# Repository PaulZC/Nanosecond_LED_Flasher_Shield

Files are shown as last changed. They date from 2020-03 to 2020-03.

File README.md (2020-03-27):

# Nanosecond LED Flasher Shield
 
A nanosecond LED flasher which provides digital control of both pulse width and LED current. Designed to aid
photomultiplier detector characterisation.
 
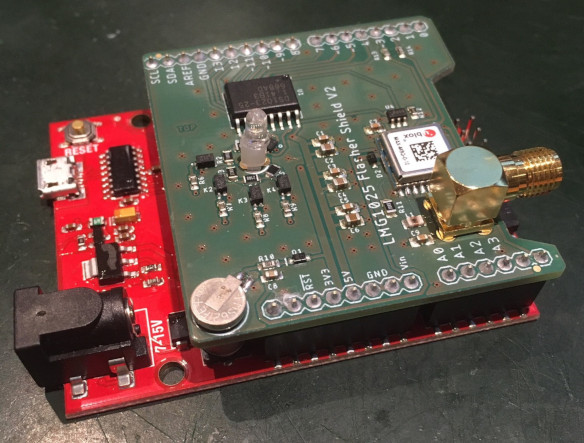
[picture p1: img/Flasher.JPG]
Flasher


The LED is driven by the new [LMG1025 from Texas Instruments](http://www.ti.com/product/LMG1025-Q1).
Designed for automotive LIDAR applications, this gate driver has typical rise and fall times of 650ps
and 850ps and can produce 5V pulse widths as short as 1.25ns.

The pulse width is controlled by a [Maxim Integrated DS1023S-25+](https://www.maximintegrated.com/en/products/analog/clock-generation-distribution/DS1023.html)
programmable timing element which can produce digitally-adjustable pulse widths of 0 to ~64ns in 0.25ns increments.

The LED current is set by five surface mount resistors connected in series, four of which can be shorted
out by [Toshiba TLP3475 photorelays](https://toshiba.semicon-storage.com/ap-en/semiconductor/product/optoelectronics/photorelay-mosfet-output/detail.TLP3475.html)
allowing the LED current to be adjusted digitally in 16 increments.

The shield also uses a [u-blox MAX-M8Q GNSS module](https://www.u-blox.com/en/product/max-m8-series) as a
signal generator to dictate the flash rate. The flash rate can be set to any frequency between 0.25Hz
and 10MHz.

The shield is designed to be mounted on a [5V ATmega328 Arduino Uno or similar](https://www.sparkfun.com/products/13975).
(Please note that the shield requires 5V I/O signals for correct operation and will not work if mounted
on a 3.3V Arduino Zero or similar.)

## Example Performance

In the image below:
- the yellow trace shows the anode voltage of a Bivar UV3TZ-400-15 UV LED being driven by the shield at maximum brightness (equivalent series resistance approx. 14 ohms) (1V per division)
- the green trace shows the corresponding fast output of a SensL J-series silicon photomultiplier (50mV per division)
- the timebase is 2 nsec per division

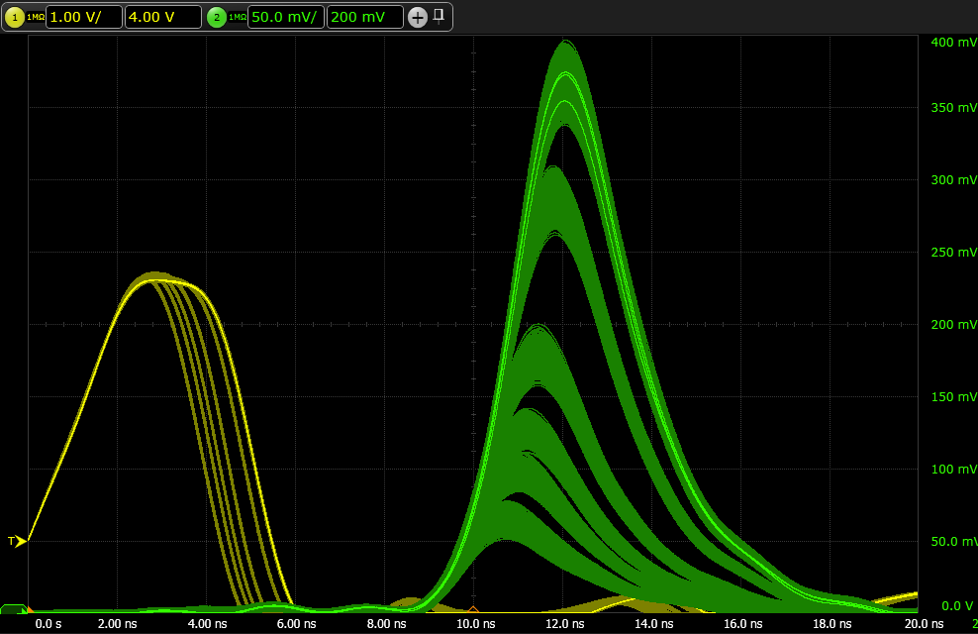
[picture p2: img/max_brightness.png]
max_brightness


The overlapping yellow traces show the LED pulse width being increased in 0.25 nsec increments. The corresponding green traces show how the peak output of
the SiPM increases in line with the LED pulse width and the number of photons emitted during each pulse.

## Repository Contents

- **/Documentation** - Documentation for the hardware and software
- **/Hardware** - BOM, schematic and Eagle PCB design files
- **/Software** - Arduino code
- **LICENSE.md** contains the licence information

## Documentation

- [Hardware overview](https://github.com/PaulZC/Nanosecond_LED_Flasher_Shield/blob/master/Documentation/Hardware/README.md): an overview of the hardware
- [Software user guide](https://github.com/PaulZC/Nanosecond_LED_Flasher_Shield/blob/master/Documentation/Software/README.md): a user guide for the Arduino code

Enjoy!

**_Paul_**

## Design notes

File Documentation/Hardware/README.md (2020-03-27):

# Nanosecond LED Flasher Shield: Hardware Overview
 
A nanosecond LED flasher which provides digital control of both pulse width and LED current. Designed to aid
photomultiplier detector characterisation.

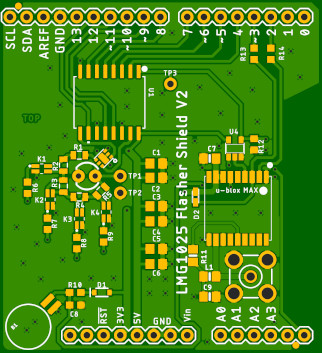
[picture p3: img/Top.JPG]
Top


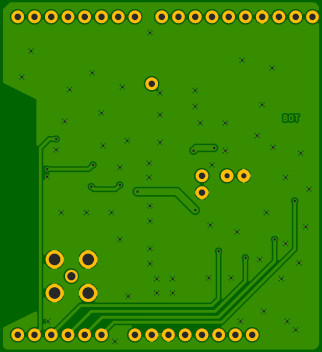
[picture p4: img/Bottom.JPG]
Bottom


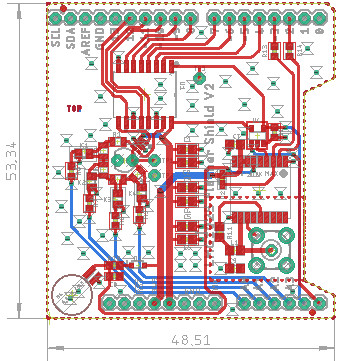
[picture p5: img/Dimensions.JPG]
Dimensions


The full schematic is available [here](https://github.com/PaulZC/Nanosecond_LED_Flasher_Shield/blob/master/Hardware/Schematic.pdf).

The BOM is available in [PDF format](https://github.com/PaulZC/Nanosecond_LED_Flasher_Shield/blob/master/Hardware/BOM.pdf)
and [ODS format](https://github.com/PaulZC/Nanosecond_LED_Flasher_Shield/blob/master/Hardware/BOM.ods).

The LED is driven by the new [LMG1025 from Texas Instruments](http://www.ti.com/product/LMG1025-Q1).
Designed for automotive LIDAR applications, this gate driver has typical rise and fall times of 650ps
and 850ps and can produce 5V pulse widths as short as 1.25ns.

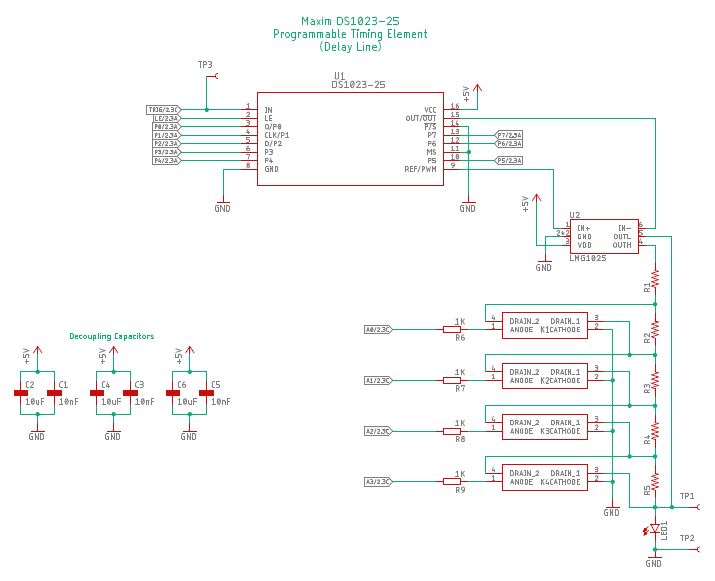
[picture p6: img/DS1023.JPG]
DS1023


The functional block diagram for the LMG1025 is:

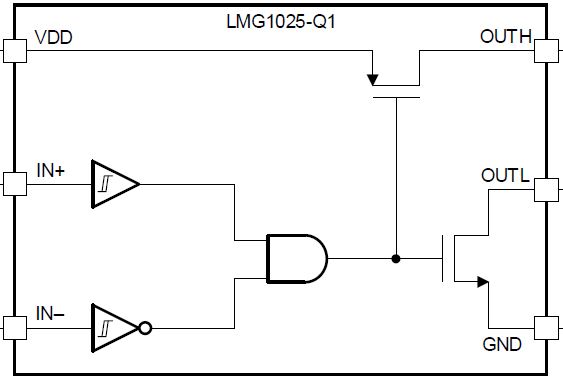
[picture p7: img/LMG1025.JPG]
LMG1025


The LMG1025 is designed to drive a GaN FET to switch a LIDAR source, but with pull-up and pull-down
current limits of 7A and 5A it can of course drive a standard or high-brightness LED directly.

The truth table for the LMG1025 is:

Truth Table

It is important to note that OUTH is pulled up to 5V only when IN+ is high and IN- is low. In each of the other
three possible states, OUTL is pulled low. We can take advantage of this by connecting OUTH to the current-limiting
resistor and OUTL directly to the LED anode. This allows the LED to be turned off very quickly.

The Maxim Integrated DS1023S-25+ is a programmable timing element with two outputs: OUT and REF. The delay between IN and
OUT is digitally-programmable from 0ns to ~64ns in 256 0.25ns increments. There is also an additional inherrent "step zero"
delay between IN and OUT caused by the propagation delay through the chip. The REF output is delayed by a small fixed delay
of approximately 1.5ns plus the same "step zero" delay. By driving the LMG1025 IN+ and IN- from REF and OUT respectively,
the LED pulse can be adjusted from essentially zero pulse width (+/-0.125ns) to a maximum of 62.5ns (64ns - 1.5ns).
The LED turns on when REF goes high, and off again when OUT goes high.

Five resistors, connected in series, are connected between the LMG1025 OUTH pin and the LED anode. By shorting out four
of these resistors in 16 permutations, the LED current can be adjusted between minimum and maximum values dictated by
the selection of resistor values. The resistors are shorted out by TLP3475 photorelays which provide fast response times
and an on-resistance of approximately 1ohm.

For example: with resistances of 10, 18, 22, 27 and 33 ohms, with the 10 ohm resistor always in circuit, it is possible to achieve
an even spread of resistance values from 13.8 ohms to 110 ohms.

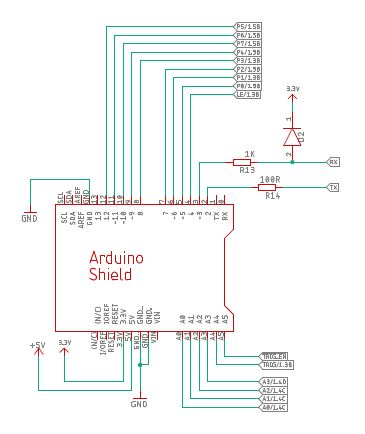
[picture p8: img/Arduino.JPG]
Arduino


The ATmega328 Arduino: controls the LED pulse width, by setting the eight parallel lines which set the DS1023 delay;
the pulse brightness, by selecting which of the four photorelays are enabled; and the pulse frequency, by setting the
frequency of the MAX-M8Q GNSS module TIMEPULSE pin. Pulse frequencies of 0.25Hz to 10MHz are possible.

The Arduino pin allocation is:
- D0: reserved for Serial Rx
- D1: reserved for Serial Tx
- D2: software serial Rx - receives GNSS data from the MAX-M8Q
- D3: software serial Tx - transmits configuration messages to the MAX-M8Q
- D4: DS1023 Latch Enable
- D5: DS1023 delay bit 0
- D6: DS1023 delay bit 1
- D7: DS1023 delay bit 2
- D8: DS1023 delay bit 3
- D9: DS1023 delay bit 4
- D10: DS1023 delay bit 7
- D11: DS1023 delay bit 6
- D12: DS1023 delay bit 5
- D13: reserved for LED_BUILTIN (but can also be used to indicate the reception of the GNSS time pulses)
- A0/D14: the photorelay for R2
- A1/D15: the photorelay for R3
- A2/D16: the photorelay for R4
- A3/D17: the photorelay for R5
- A4/D18: the MAX-M8Q time pulse (to allow the LED current to be changed between LED pulses)
- A5/D19: enables / disables LED pulses via the 74HCT1G125 buffer

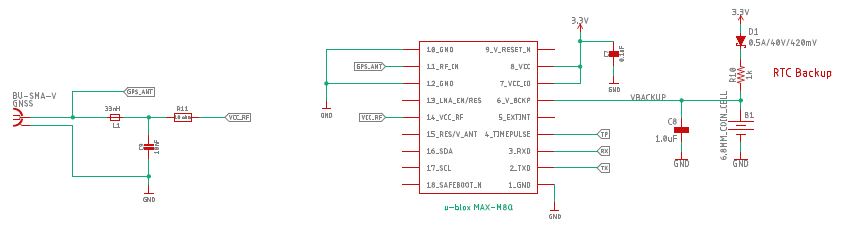
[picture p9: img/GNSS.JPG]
GNSS


The time pulse signal produced by the MAX-M8Q GNSS receiver is used to trigger the DS1023. The frequency of the time pulse
signal can be defined by the Arduino code via software serial (D2 and D3). The LED flashes on the rising edge of the time pulse.
The time pulse signal is connected to the Arduino pin A4/D18 so that the LED current can be adjusted between pulses on the
falling edge of the signal. It is possible to change the current for adjacent LED pulses from one of the sixteen permutations
to any other. The Arduino code can produce repetitive pulse patterns using any of the sixteen states.

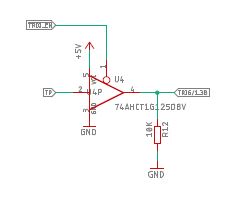
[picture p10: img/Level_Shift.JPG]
Level_Shift


The MAX-M8Q is a 3.3V device. A 74HCT1G125 buffer is used to convert the 3.3V time pulses to 5V for the DS1023. The enable pin
of the buffer is connected to Arduino pin A5/D19 such that pulses can be skipped or disabled as required.

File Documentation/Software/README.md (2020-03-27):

# Nanosecond LED Flasher Shield: Software Overview
 
The Arduino code for the nanosecond flasher is available [here](https://github.com/PaulZC/Nanosecond_LED_Flasher_Shield/tree/master/Software/LMG1025_Flasher).

Please ensure you select _Arduino Uno_ as the Board.

The code has been deliberately kept very simple. It begins by setting the MAX-M8Q time pulse pin to the desired frequency.
You will find definitions in the code for frequencies of 60Hz, 500Hz, 1kHz, 10kHz, 100kHz and 1MHz.

Also defined in the code are sequences of LED pulse brightnesses (currents) that can be used if desired. By default,
the brightness sequence is disabled. You can enable one by uncommenting _#define useSequence_ plus one of the
definitions for _sequence_.

The LED pulse width and current can be configured by sending a serial string to the Arduino, via the Serial Monitor.
The Serial baud rate should be set to 9600. Set the line ending to LF. The serial data format is:
- ASCII <                : 3C Hex
- Pulse Delay P7 (MSB)   : ASCII 0 or 1 (30 or 31 Hex)
- Pulse Delay P6         : ASCII 0 or 1 (30 or 31 Hex)
- Pulse Delay P5         : ASCII 0 or 1 (30 or 31 Hex)
- Pulse Delay P4         : ASCII 0 or 1 (30 or 31 Hex)
- Pulse Delay P3         : ASCII 0 or 1 (30 or 31 Hex)
- Pulse Delay P2         : ASCII 0 or 1 (30 or 31 Hex)
- Pulse Delay P1         : ASCII 0 or 1 (30 or 31 Hex)
- Pulse Delay P0 (LSB)   : ASCII 0 or 1 (30 or 31 Hex)
- LED R5                 : ASCII 0 or 1 (30 or 31 Hex) (0 = R is in circuit; 1 = R is shorted) (R5 is >> R2)
- LED R4                 : ASCII 0 or 1 (30 or 31 Hex) (0 = R is in circuit; 1 = R is shorted)
- LED R3                 : ASCII 0 or 1 (30 or 31 Hex) (0 = R is in circuit; 1 = R is shorted)
- LED R2                 : ASCII 0 or 1 (30 or 31 Hex) (0 = R is in circuit; 1 = R is shorted) (R2 is << R5)
- ASCII >                : 3E Hex
- LF                     : 0A Hex

e.g.:  <000100001111>\n will produce ~2.5ns pulses ((16 x 0.25ns) - 1.5ns) of maximum brightness (all four photorelays are on)

A shorter message can be sent if you only want to change the pulse width:
- ASCII <                : 3C Hex
- Pulse Delay P7 (MSB)   : ASCII 0 or 1 (30 or 31 Hex)
- Pulse Delay P6         : ASCII 0 or 1 (30 or 31 Hex)
- Pulse Delay P5         : ASCII 0 or 1 (30 or 31 Hex)
- Pulse Delay P4         : ASCII 0 or 1 (30 or 31 Hex)
- Pulse Delay P3         : ASCII 0 or 1 (30 or 31 Hex)
- Pulse Delay P2         : ASCII 0 or 1 (30 or 31 Hex)
- Pulse Delay P1         : ASCII 0 or 1 (30 or 31 Hex)
- Pulse Delay P0 (LSB)   : ASCII 0 or 1 (30 or 31 Hex)
- ASCII >                : 3E Hex
- LF                     : 0A Hex

e.g.:  <001000001111>\n will produce ~6.5ns pulses ((32 x 0.25ns) - 1.5ns)

The code will: parse the incoming serial data, check the format is valid, set the DS1023 pulse width,
and the state of the four photorelays.

The rise time of the LED forward voltage will depend on the resistance value. More resistance equals
slower rise times as well as lower current (and lower peak forward voltage too). The actual pulse width,
in terms of how long the LED is actually emitting photons for, is equal to the amount of time the forward voltage
exceeds approximately 3.1V (for the Bivar UV3TZ-400-15 400nm InGaN/Sapphire UV LED).

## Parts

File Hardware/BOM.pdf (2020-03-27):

LMG1025_Flasher_Shield

Page 1

Name X | Y | Angle Package | Value | Comments
FD1 | 2.29 52.45 | 0 FIDUCIAL
FD2 | 44.45 | 1.02 | 0 FIDUCIAL
B1 | 7.25 | 7.25 | 45 | MS621FE-FL11E | 1614634 | Rechargeable 3V 6.8mm Coin Cell Seiko MS621FE-FL11E
C1 | 23.24 28.58 | 0 0805 | 10nF | 2496939 | SMD Capacitor 10nF 50V 0805 +/-10% X7R
C2 | 23.24 26.42 | 0 0805 | 10uF | 1759421 | SMD Capacitor 10uF 10V 0805 +80% -20% Y5V
C3 | 23.24 | 22.1 | 0 0805 | 10nF | 2496939 | SMD Capacitor 10nF 50V 0805 +/-10% X7R
C4 | 23.24 19.81 | 0 0805 | 10uF | 1759421 | SMD Capacitor 10uF 10V 0805 +80% -20% Y5V
C5 | 23.24 15.62 | 0 0805 | 10nF | 2496939 | SMD Capacitor 10nF 50V 0805 +/-10% X7R
C6 | 23.24 13.34 | 0 0805 | 10uF | 1759421 | SMD Capacitor 10uF 10V 0805 +80% -20% Y5V
C7 | 31.37 29.34 | 180 0805 | 0.1uF | 2496944 | SMD Capacitor 100nF 50V 0805 +/-10% X7R
C8 | 10.92 | 7.11 | 0 0603 | 1.0uF | 1327684 | SMD Capacitor 1uF 10V 0603 +/-10% X5R
C9 | 31.37 | 8.38 | 0 0805 | 10nF | 2496939 | SMD Capacitor 10nF 50V 0805 +/-10% X7R
D1 | 14.99 | 9.02 | 0 SOD-323 | PMEG4005EJ | 1757776 | Schottky Rectifier 40V 500mA Nexperia PMEG4005EJ
D2 | 29.21 | 23.5 | 270 SOD-323 | PMEG4005EJ | 1757776 | Schottky Rectifier 40V 500mA Nexperia PMEG4005EJ
K1 | 5.84 27.79 | 270 | TLP3475 | Toshiba TLP3475 Photorelay (not TLP3475R) Mouser: 757-TLP3475TPF
K2 | 7.13 23.11 | 0 | TLP3475 | Toshiba TLP3475 Photorelay (not TLP3475R) Mouser: 757-TLP3475TPF
K3 | 11.58 20.19 | 0 | TLP3475 | Toshiba TLP3475 Photorelay (not TLP3475R) Mouser: 757-TLP3475TPF
K4 | 15.64 21.21 | 0 | TLP3475 | Toshiba TLP3475 Photorelay (not TLP3475R) Mouser: 757-TLP3475TPF
L1 | 31.37 11.43 | 0 0805 | 0805HT-33NTGLB | 2286465 | Surface Mount High Frequency Inductor; 0805; 33 nH; 600 mA
R1 | 11.56 29.85 | 0 0805 | Select on test: suggested value 10R
R2 | 9.14 28.32 | 90 0805 | Select on test: suggested value 18R
R3 | 9.14 25.15 | 90 0805 | Select on test: suggested value 22R
R4 | 11.56 | 23.5 | 180 0805 | | | Select on test: suggested value 27R
R5 | 14.86 24.38 | 225 0805 | Select on test: suggested value 33R
R6 | 3.68 24.89 | 270 0603 | 1K | 2447272 | SMD Chip Resistor; Thick Film; 1k; 75V; 0603; 100mW
R7 | 6.73 19.43 | 270 0603 | 1K | 2447272 | SMD Chip Resistor; Thick Film; 1k; 75V; 0603; 100mW
R8 | 11.18 16.51 | 270 0603 | 1K | 2447272 | SMD Chip Resistor; Thick Film; 1k; 75V; 0603; 100mW
R9 | 15.24 17.53 | 270 0603 | 1K | 2447272 | SMD Chip Resistor; Thick Film; 1k; 75V; 0603; 100mW
R10 | 10.92 | 9.02 | 0 0603 | 1k | 2447272 | SMD Chip Resistor; Thick Film; 1k; 75V; 0603; 100mW
R11 | 28.83 14.61 | 90 0805 | 10R | 1469859 | SMD Chip Resistor; Thick Film; 10 ohm; 150V; 0805; 100mW
R12 | 38.1 | 31.5 | 270 0603 | 10K | 2447230 | SMD Chip Resistor; Thick Film; 10K; 75V; 0603; 100mW
R13 | 38.1 45.21 | 90 0603 | 1K | 2447272 | SMD Chip Resistor; Thick Film; 1k; 75V; 0603; 100mW
R14 | 40.64 45.21 | 90 0603 | 100R | 2447227 | SMD Chip Resistor; Thick Film; 100 ohm; 75V; 0603; 100mW
U1 | 16.13 37.85 | 270 WSOIC-16 | DS1023S-25+ | 2516605 | Maxim Delay Line; 256 taps; 250ps delay/tap
U2 | 15.24 29.34 | 135 LMG1025 | LMG1025
U3 | 35.61 21.79 | 90 MAX-M8 | MAX-M8
U4 | 35.18 30.87 | 0 SOT23-5 | 74AHCT1G125DBV 1085267 | Buffer / Line Driver

Farnell /
Element 14

TI LMG1025: https://www.ti.com/product/LMG1025-Q1
u-blox MAX-M8Q GNSS module: https://www.u-blox.com/en/product/max-m8-series

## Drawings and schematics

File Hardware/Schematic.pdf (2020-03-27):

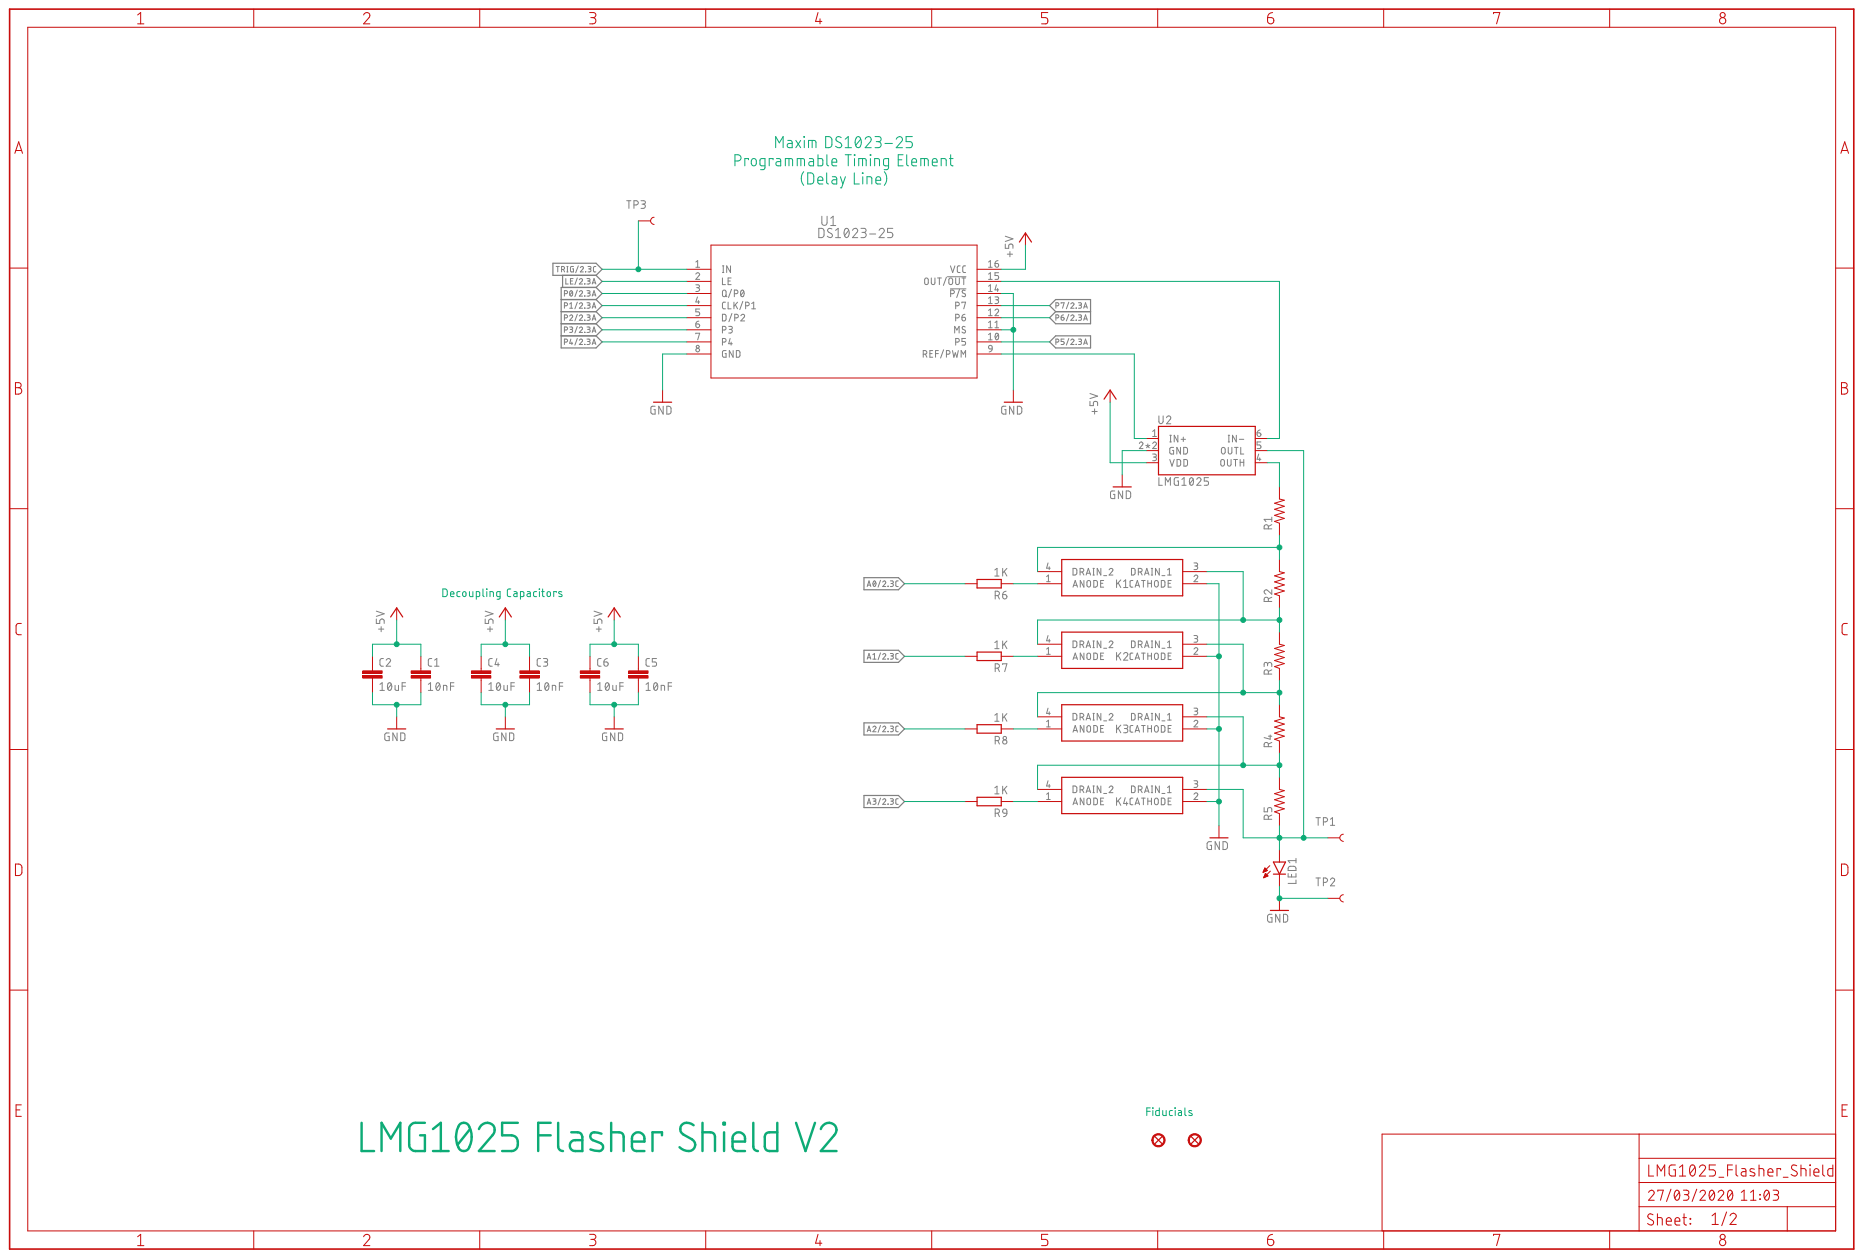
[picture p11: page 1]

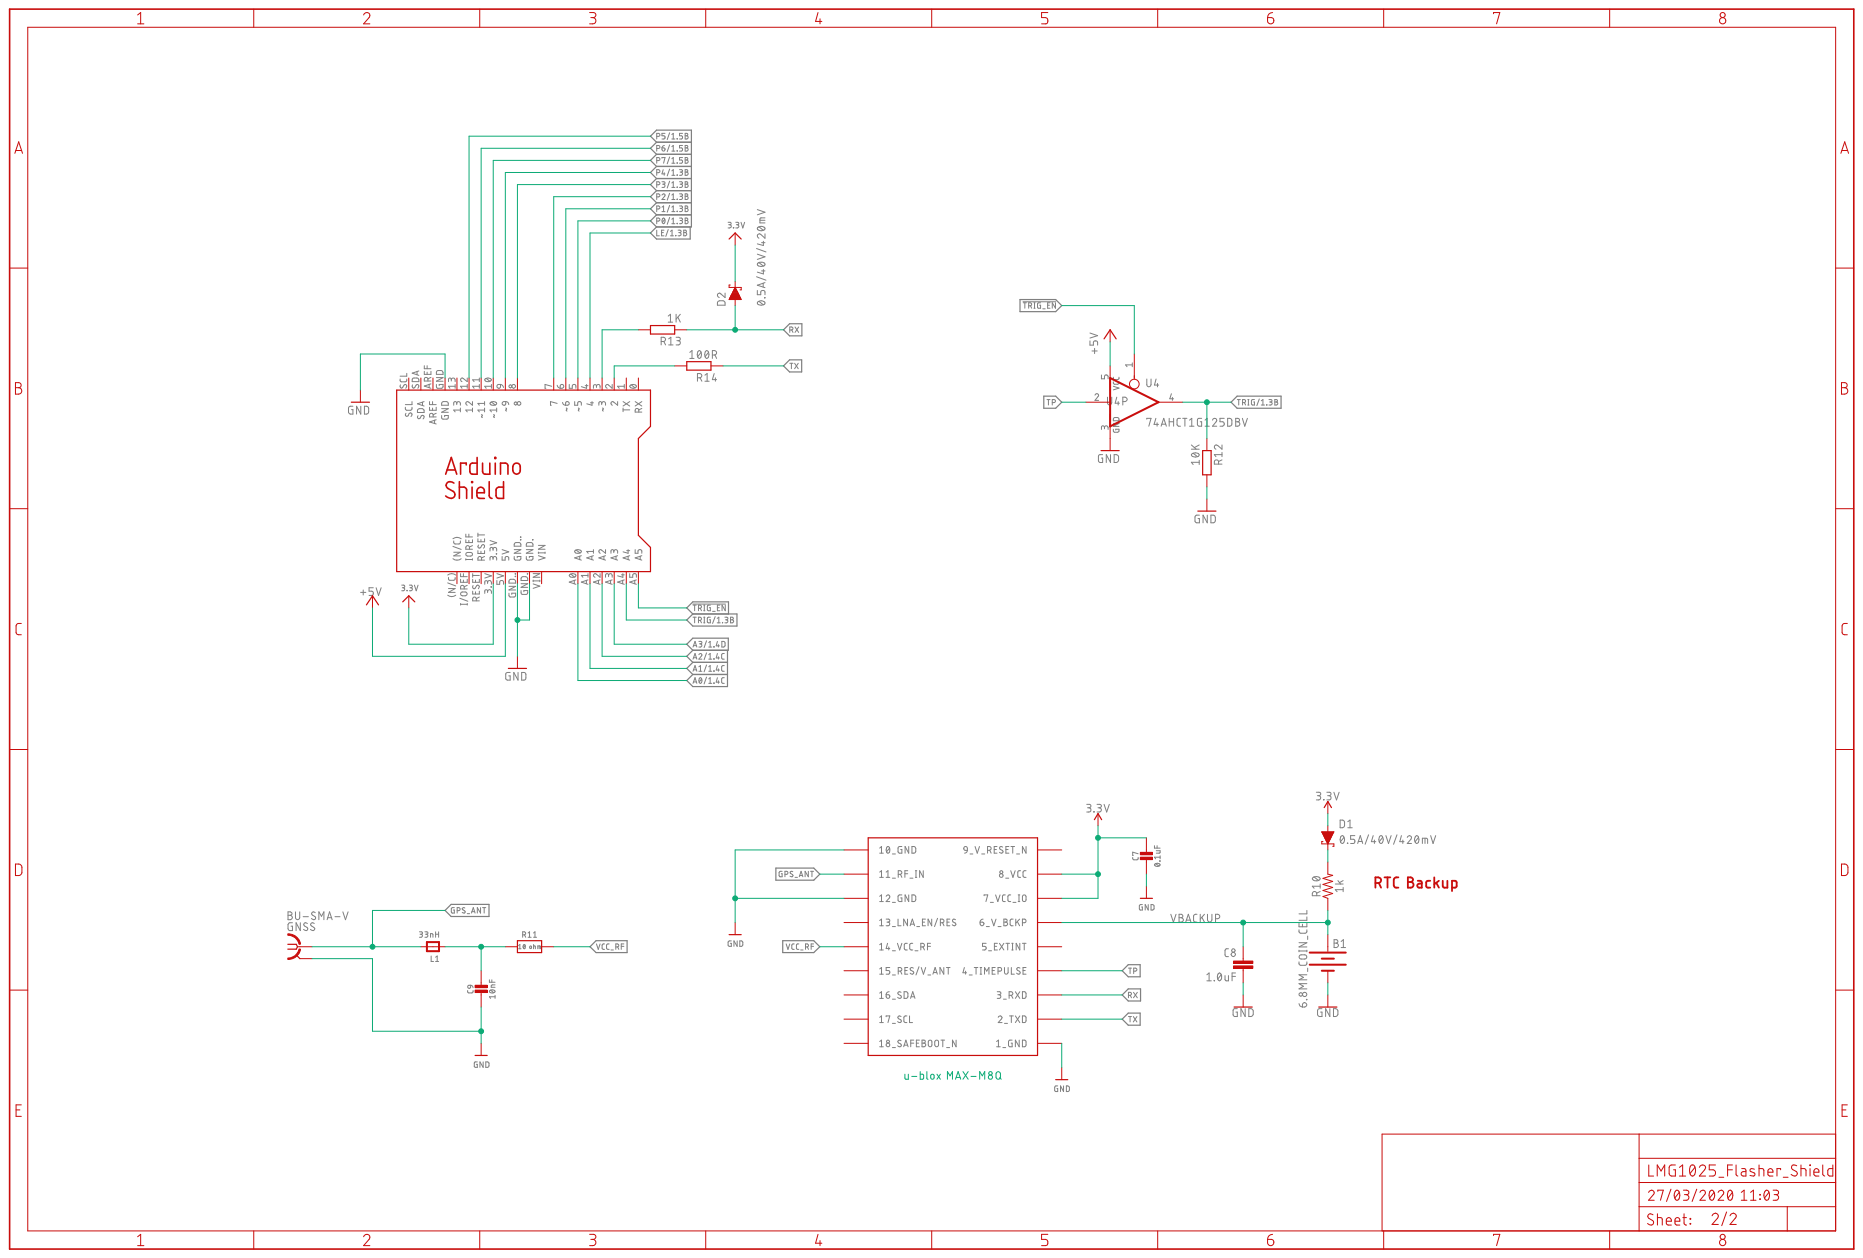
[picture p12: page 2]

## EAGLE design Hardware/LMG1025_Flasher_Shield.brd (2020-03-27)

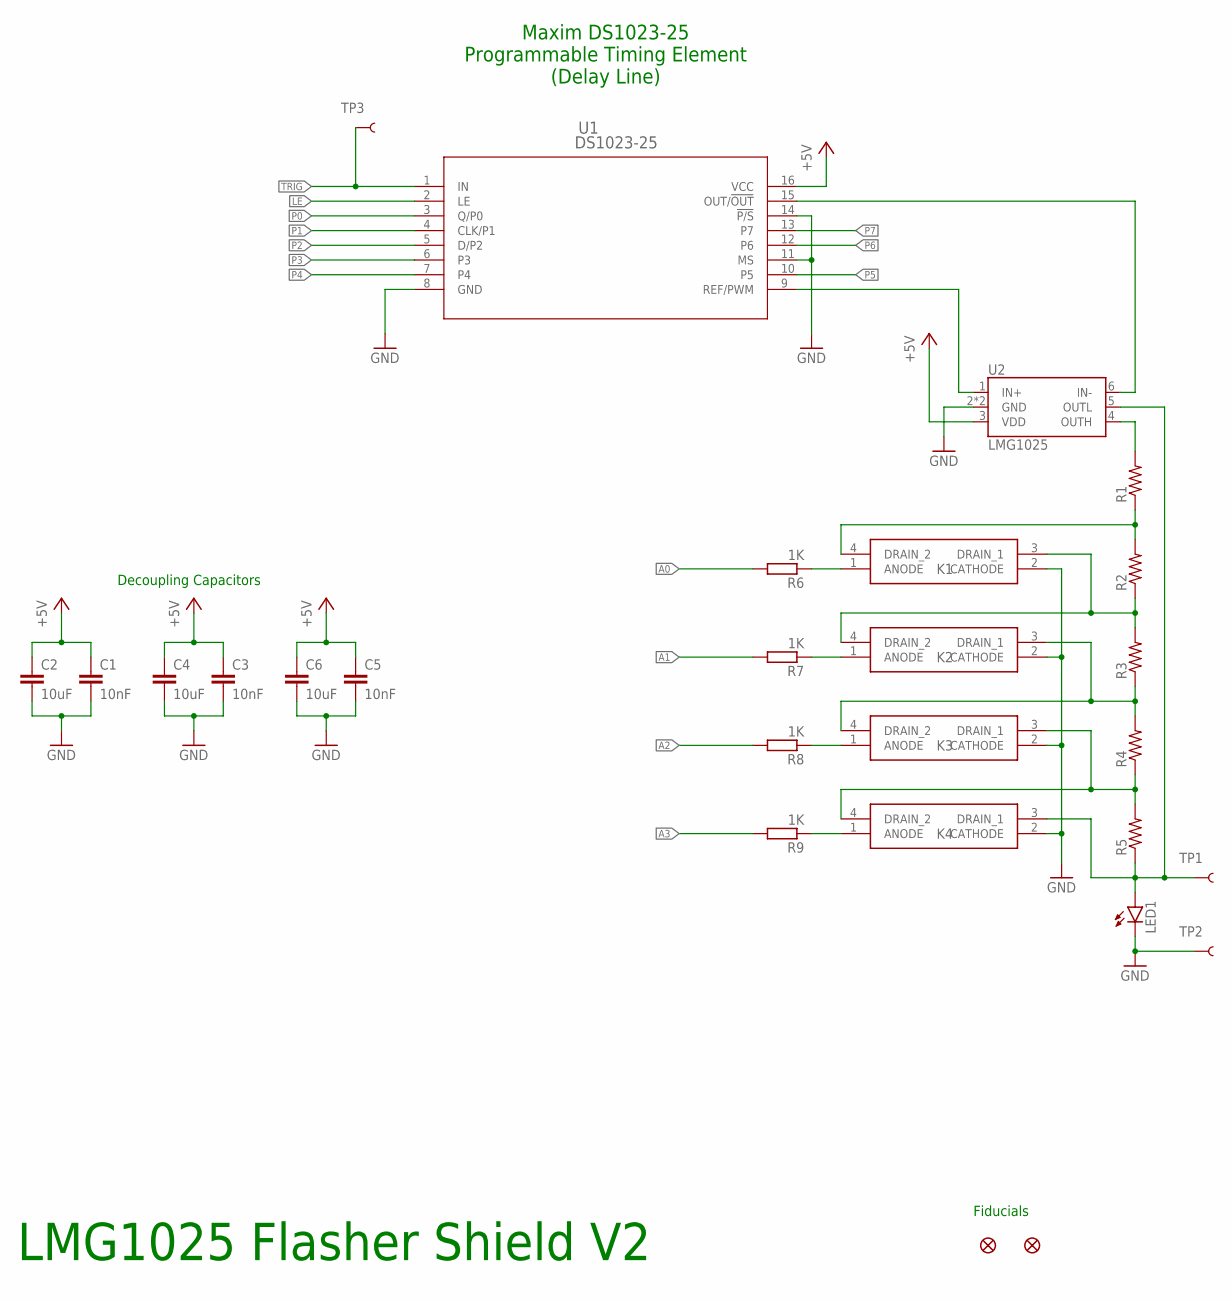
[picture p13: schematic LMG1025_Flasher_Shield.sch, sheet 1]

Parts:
C1, C3, C5: 10nF; C0805
C2, C4, C6: 10uF; C0805
FD1, FD2: FIDUCIAL1X2; FIDUCIAL-1X2
K1, K2, K3, K4: TLP3475R(TP,F; TLP3475RTPF
LED1: LED3MM
R1, R2, R3, R4, R5: RESISTOR0805-RES; 0805
R6, R7, R8, R9: 1K; R0603
TP1, TP2, TP3: TEST-POINTPOGO_PTH; 1X01_NO_SILK
U1: DS1023-25; 21-0042B_16
U2: LMG1025

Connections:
+5V: C1.1, C2.1, C3.1, C4.1, C5.1, C6.1, U1.16 (VCC), U2.3 (VDD); also elsewhere on the board
A0: R6.2; also elsewhere on the board
A1: R7.2; also elsewhere on the board
A2: R8.2; also elsewhere on the board
A3: R9.2; also elsewhere on the board
GND: C1.2, C2.2, C3.2, C4.2, C5.2, C6.2, K1.2 (CATHODE), K2.2 (CATHODE), K3.2 (CATHODE), K4.2 (CATHODE), LED1.K (C), TP2.1, U1.8 (GND), U1.11 (MS), U1.14 (!P/S), U2.2 (GND), U2.PAD (GND); also elsewhere on the board
LE: U1.2 (LE); also elsewhere on the board
unnamed: K1.4 (DRAIN_2), R1.1, R2.2
unnamed: K1.3 (DRAIN_1), K2.4 (DRAIN_2), R2.1, R3.2
unnamed: K4.3 (DRAIN_1), LED1.A, R5.1, TP1.1, U2.5 (OUTL)
unnamed: K2.3 (DRAIN_1), K3.4 (DRAIN_2), R3.1, R4.2
unnamed: K3.3 (DRAIN_1), K4.4 (DRAIN_2), R4.1, R5.2
unnamed: R1.2, U2.4 (OUTH)
unnamed: K1.1 (ANODE), R6.1
unnamed: K2.1 (ANODE), R7.1
unnamed: K3.1 (ANODE), R8.1
unnamed: K4.1 (ANODE), R9.1
unnamed: U1.9 (REF/PWM), U2.1 (IN+)
unnamed: U1.15 (OUT/!OUT), U2.6 (IN-)
P0: U1.3 (Q/P0); also elsewhere on the board
P1: U1.4 (CLK/P1); also elsewhere on the board
P2: U1.5 (D/P2); also elsewhere on the board
P3: U1.6 (P3); also elsewhere on the board
P4: U1.7 (P4); also elsewhere on the board
P5: U1.10 (P5); also elsewhere on the board
P6: U1.12 (P6); also elsewhere on the board
P7: U1.13 (P7); also elsewhere on the board
TRIG: TP3.1, U1.1 (IN); also elsewhere on the board

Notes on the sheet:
LMG1025 Flasher Shield V2
Fiducials
Decoupling Capacitors
Maxim DS1023-25 Programmable Timing Element (Delay Line)

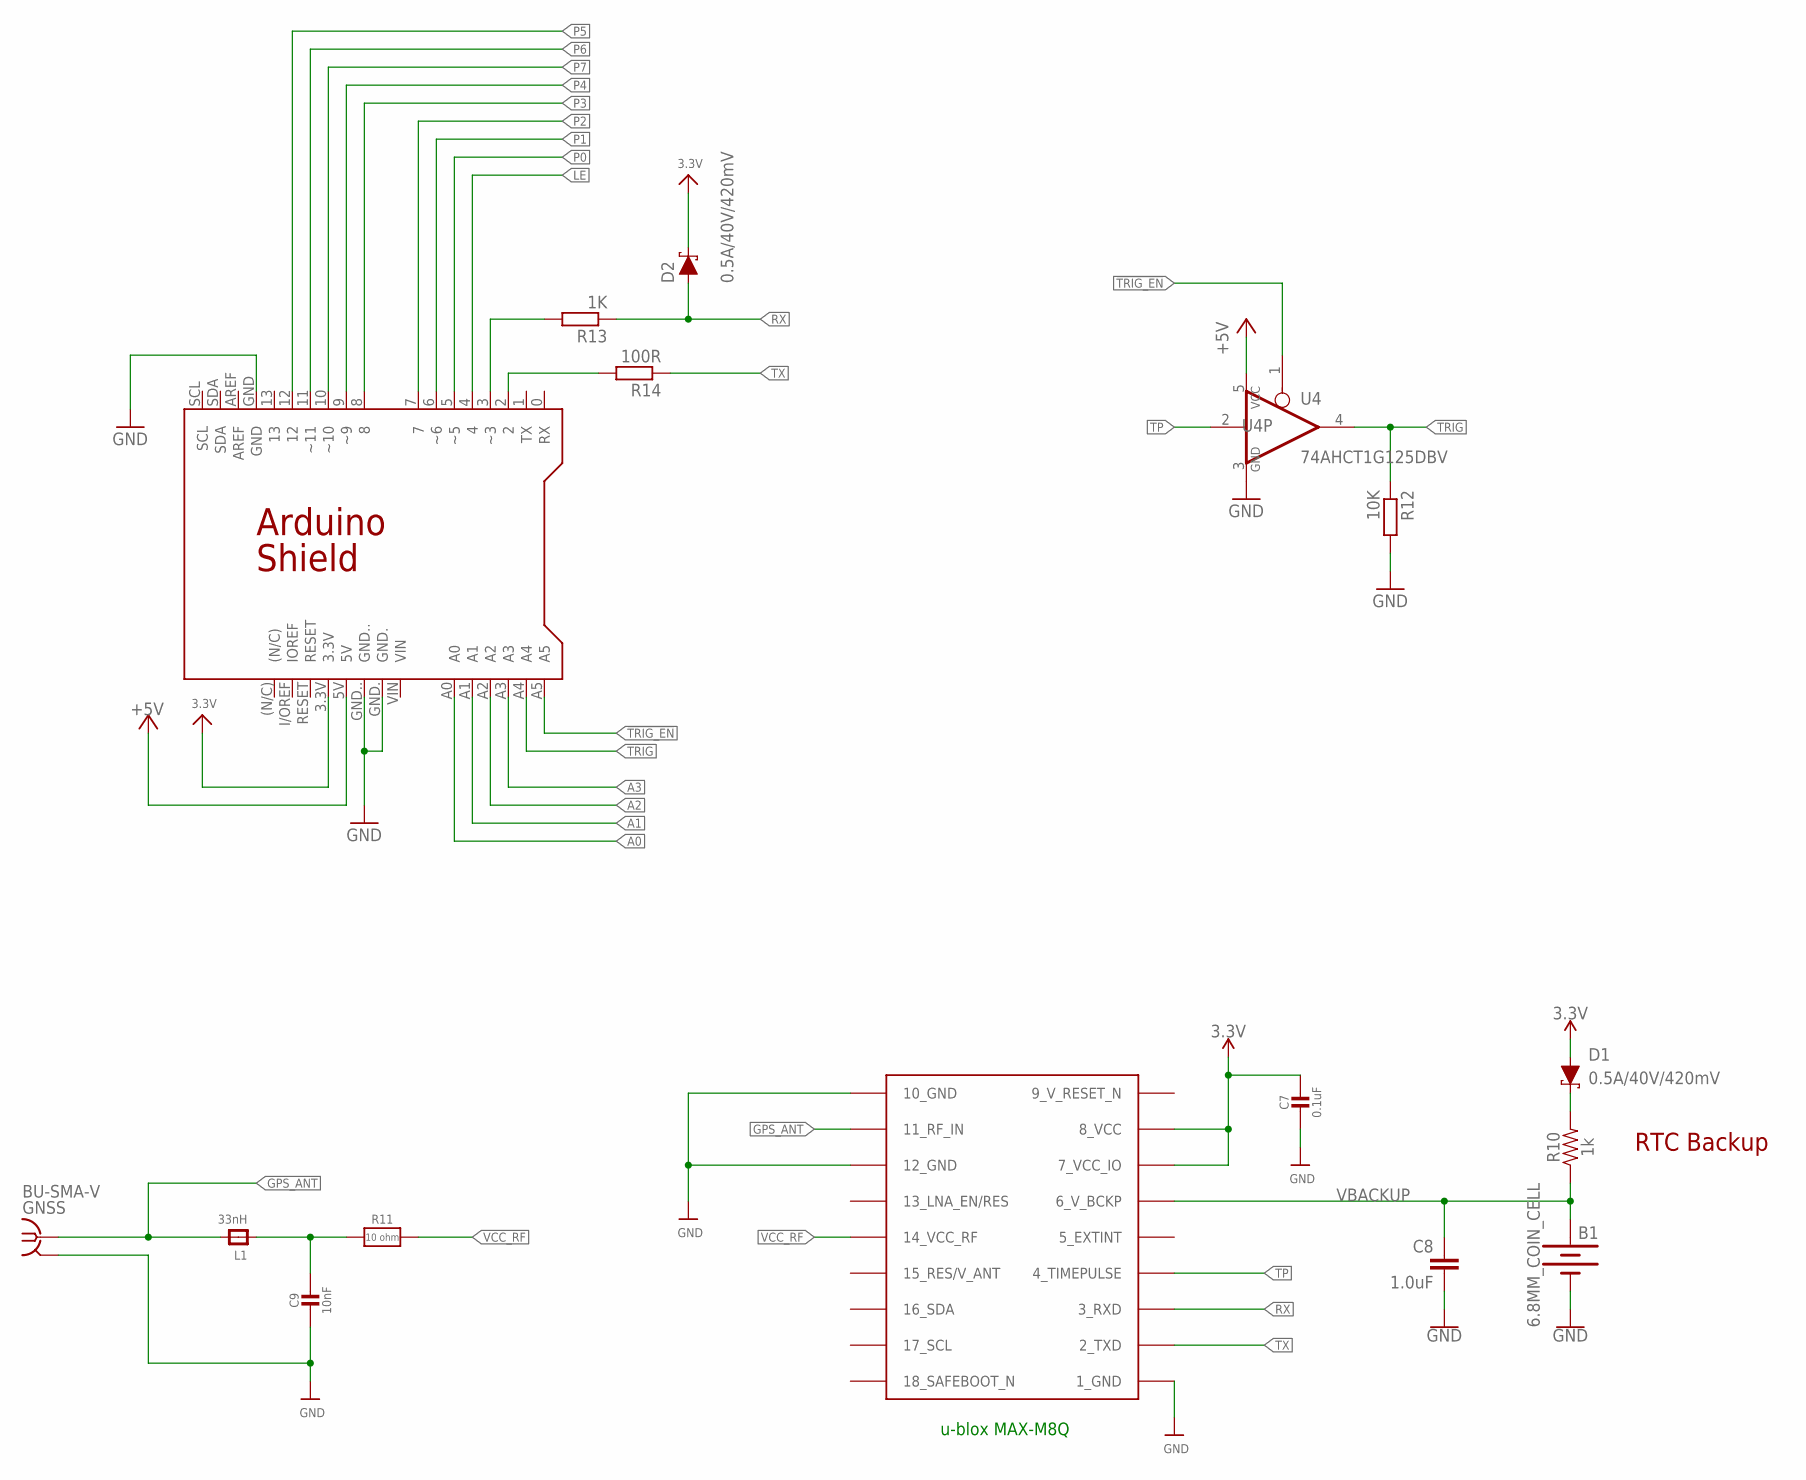
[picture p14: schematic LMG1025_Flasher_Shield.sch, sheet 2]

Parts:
B1: 6.8MM_COIN_CELL; BATTCON-6.8MM
C7: 0.1uF; 0805-NO
C8: 1.0uF; 0603
C9: 10nF; 0805-NO
D1, D2: 0.5A/40V/420mV; SOD-323
GNSS: BU-SMA-V
L1: 33nH; 0805-NO
PCB1: CHEC_LED_DRIVER_SHIELD
R10: 1k; 0603@1
R11: 10 ohm; 0805-NO
R12: 10K; R0603
R13: 1K; R0603
R14: 100R; R0603
U3: MAX-M8
U4: 74AHCT1G125DBV; SOT23-5

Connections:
3.3V: C7.1, D1.A, D2.C, PCB1.3.3V, U3.7_VCC_IO, U3.8_VCC
9_V_RESET_N: U3.9_RESET_N (9_V_RESET_N)
!TRIG_EN: PCB1.A5, U4.1 (OE)
+5V: PCB1.5V, U4.5 (VCC); also elsewhere on the board
A0: PCB1.A0; also elsewhere on the board
A1: PCB1.A1; also elsewhere on the board
A2: PCB1.A2; also elsewhere on the board
A3: PCB1.A3; also elsewhere on the board
GND: B1.-, C7.2, C8.2, C9.2, GNSS.2, GNSS.3 (2), GNSS.4 (2), GNSS.5 (2), PCB1.GND, PCB1.GND., PCB1.GND.., R12.2, U3.1_GND, U3.10_GND, U3.12_GND, U4.3 (GND); also elsewhere on the board
GPS_ANT: GNSS.1, L1.2, U3.11_RF_IN
LE: PCB1.4; also elsewhere on the board
unnamed: PCB1.3 (~3), R13.2
unnamed: C9.1, L1.1, R11.1
unnamed: D1.C, R10.2
unnamed: PCB1.2, R14.2
P0: PCB1.5 (~5); also elsewhere on the board
P1: PCB1.6 (~6); also elsewhere on the board
P2: PCB1.7; also elsewhere on the board
P3: PCB1.8; also elsewhere on the board
P4: PCB1.9 (~9); also elsewhere on the board
P5: PCB1.12; also elsewhere on the board
P6: PCB1.11 (~11); also elsewhere on the board
P7: PCB1.10 (~10); also elsewhere on the board
RX: D2.A, R13.1, U3.3_RXD
TP: U3.4_TIMEPULSE, U4.2 (I)
TRIG: PCB1.A4, R12.1, U4.4 (O); also elsewhere on the board
TX: R14.1, U3.2_TXD
VBACKUP: B1.+, C8.1, R10.1, U3.6_V_BCKP
VCC_RF: R11.2, U3.14_VCC_RF

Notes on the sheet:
u-blox MAX-M8Q
RTC Backup

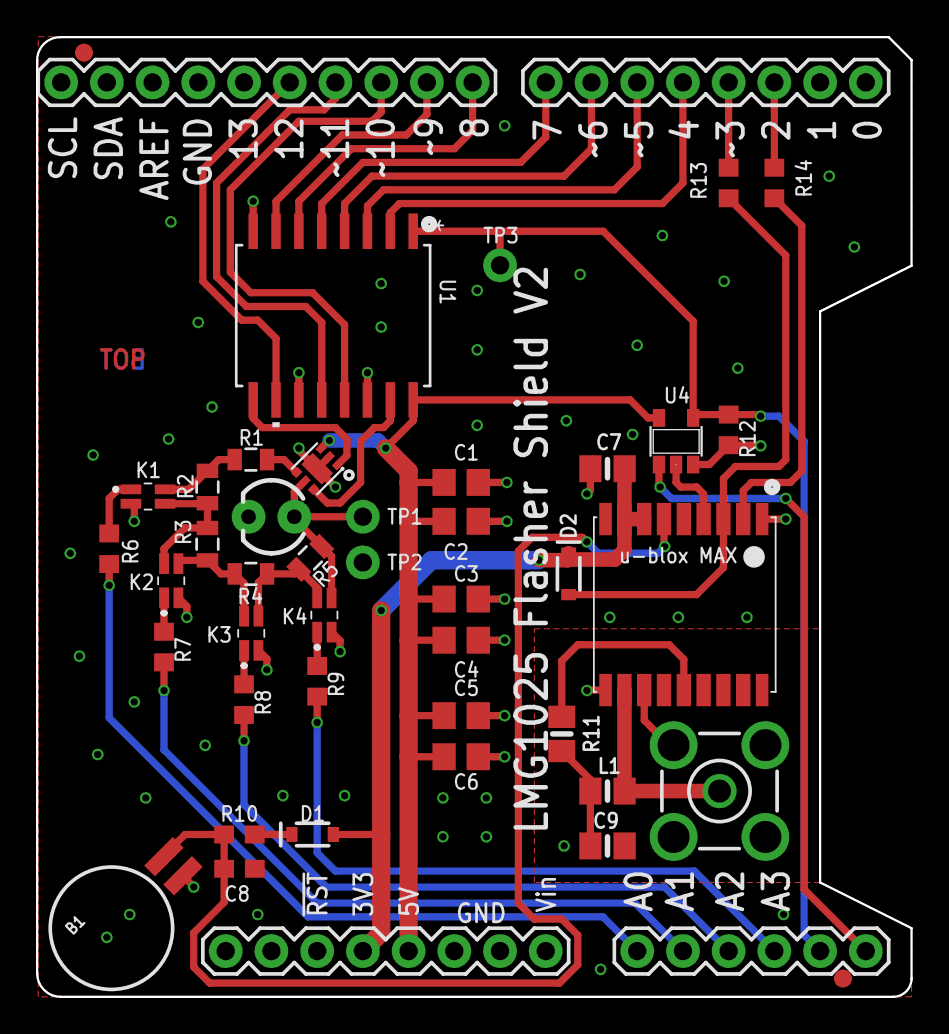
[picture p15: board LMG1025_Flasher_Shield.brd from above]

Board: 2 copper layers, 48.6 x 53.3 mm, 43 parts (0 on the bottom side), 40 nets.

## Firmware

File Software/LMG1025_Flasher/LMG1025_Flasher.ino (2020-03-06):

// Code for the LMG1025 Flasher Shield (V2) for the SparkFun RedBoard Qwiic (5V) DEV-15123

// The flash pulse width is set by a Maxim DS1023-25 Programmable Timing Element (Delay Line)

// The LED current is controlled by setting A0-A3 high/low.
// High will short the corresponding resistor to increase the LED current.

// The MAX-M8Q is connected to D2/D3 for Software Serial.
// The timepulse pin sets the flash rate.

// Serial data is 9600 Baud
// The serial data format is:
//
// ASCII <                : 3C Hex
// Pulse Delay P7 (MSB)   : ASCII 0 or 1 (30 or 31 Hex)
// Pulse Delay P6         : ASCII 0 or 1 (30 or 31 Hex)
// Pulse Delay P5         : ASCII 0 or 1 (30 or 31 Hex)
// Pulse Delay P4         : ASCII 0 or 1 (30 or 31 Hex)
// Pulse Delay P3         : ASCII 0 or 1 (30 or 31 Hex)
// Pulse Delay P2         : ASCII 0 or 1 (30 or 31 Hex)
// Pulse Delay P1         : ASCII 0 or 1 (30 or 31 Hex)
// Pulse Delay P0 (LSB)   : ASCII 0 or 1 (30 or 31 Hex)
// LED R5                 : ASCII 0 or 1 (30 or 31 Hex) (0 = R is in circuit; 1 = R is shorted) (R5 is >> R2)
// LED R4                 : ASCII 0 or 1 (30 or 31 Hex) (0 = R is in circuit; 1 = R is shorted)
// LED R3                 : ASCII 0 or 1 (30 or 31 Hex) (0 = R is in circuit; 1 = R is shorted)
// LED R2                 : ASCII 0 or 1 (30 or 31 Hex) (0 = R is in circuit; 1 = R is shorted) (R2 is << R5)
// ASCII >                : 3E Hex
// LF                     : 0A Hex
//
// 15 bytes total
//
// - or -
//
// ASCII <                : 3C Hex
// Pulse Delay P7 (MSB)   : ASCII 0 or 1 (30 or 31 Hex)
// Pulse Delay P6         : ASCII 0 or 1 (30 or 31 Hex)
// Pulse Delay P5         : ASCII 0 or 1 (30 or 31 Hex)
// Pulse Delay P4         : ASCII 0 or 1 (30 or 31 Hex)
// Pulse Delay P3         : ASCII 0 or 1 (30 or 31 Hex)
// Pulse Delay P2         : ASCII 0 or 1 (30 or 31 Hex)
// Pulse Delay P1         : ASCII 0 or 1 (30 or 31 Hex)
// Pulse Delay P0 (LSB)   : ASCII 0 or 1 (30 or 31 Hex)
// ASCII >                : 3E Hex
// LF                     : 0A Hex
//
// 11 bytes total
//
//
// The code can be configured to automatically loop through a pre-defined sequence of LED currents while keeping
// the pulse width constant.

//#define useSequence // Uncomment this line to enable a sequence of LED currents
// Then uncomment _one_ sequence definition:
// All 16 states from minimum brightness (B0000) to maximum brightness (B1111)
const byte seqLength = 16; const byte sequence[16] = {B0000, B0001, B0010, B0011, B0100, B0101, B0110, B0111, B1000, B1001, B1010, B1011, B1100, B1101, B1110, B1111};
// 5 states: shorting out none or one of the four resistors in turn ('dim')
//const byte seqLength = 5; const byte sequence[5] = {B0000, B0001, B0010, B0100, B1000};
// 5 states: shorting out all or three of the four resistors in turn ('bright')
//const byte seqLength = 5; const byte sequence[5] = {B1111, B1110, B1101, B1011, B0111};
// 5 states: maximum to minimum resistance in four ~equal steps (assumes R1-R5 are: 10/18/22/27/33) (Rs are: 110,89,62.9,39.9,13.8 assuming 1R for the photorelays)
//const byte seqLength = 5; const byte sequence[5] = {B0000, B0010, B0110, B1011, B1111};
// 4 states: shorting out none or R2/R3 in turn (the four dimmest combinations)
//const byte seqLength = 4; const byte sequence[4] = {B0000, B0001, B0010, B0011};
// 4 states: shorting out R4/R5 and R2/R3 in turn (the four brightest combinations)
//const byte seqLength = 4; const byte sequence[4] = {B1111, B1110, B1101, B1100};
// 2 states: shorting out none or all of the resistors in turn (dimmest and brightest)
//const byte seqLength = 2; const byte sequence[4] = {B0000, B1111};

static byte seqStep = 0; // Used to store the sequence step (0 : seqLength-1)

#define BUFFER_LENGTH 15 // Serial buffer length
#define SHORT_MESSAGE 4 // A short message is this much sorter than BUFFER_LENGTH
static unsigned char RX_BUFFER[BUFFER_LENGTH]; // Serial buffer

#define TRIG_BUFFER_LENGTH 4
#define HALF_TRIG_BUFFER_LENGTH 2
byte TRIG_BUFFER[TRIG_BUFFER_LENGTH]; // Buffer to store the state of TRIG_IN for edge detection

// Maxim DS1023-25 Pin Definitions:
#define DELAY0 5    // P0 (LSB) : D5      : Delay Bit 0
#define DELAY1 6    // P1       : D6      : Delay Bit 1
#define DELAY2 7    // P2       : D7      : Delay Bit 2
#define DELAY3 8    // P3       : D8      : Delay Bit 3
#define DELAY4 9    // P4       : D9      : Delay Bit 4
#define DELAY5 12   // P5       : D12     : Delay Bit 5
#define DELAY6 11   // P6       : D11     : Delay Bit 6
#define DELAY7 10   // P7 (MSB) : D10     : Delay Bit 7
#define TRIG_EN 19  // 74AHCT1G125 Enable (Active Low) : A5/D19
#define DELAY_LE 4  // LE       : D4      : Normally high; low latches the delay
#define TRIG_IN 18  // A4/D18   : Trigger signal from the MAX-M8Q (used to control the flash rate and current sequence)
//#define TRIG_OUT 13 // D13 : Used to confirm that TRIG_IN is being received correctly (comment out if not required)

// LED Resistor Control: HIGH = R is in circuit; LOW = R is shorted
#define LED_R5  17 // LED R5   : A3/D17
#define LED_R4  16 // LED R4   : A2/D16
#define LED_R3  15 // LED R3   : A1/D15
#define LED_R2  14 // LED R2   : A0/D14

// Software Serial for the MAX-M8Q GNSS
#include <SoftwareSerial.h>
SoftwareSerial mySerial(2, 3); // RX, TX
//#define echoGNSS // Uncomment this line to echo the GNSS data to Serial
#define endSerial // Uncomment this to disable the software serial after the GNSS has been configured (overrides echoGNSS)

// Update an output pin
void update_pin(int pin, unsigned char val) {
  if (pin >= 0) {
    bool state = val & 0x01;
    digitalWrite(pin, state);
  }
}

// Update an output pin inverted
void update_pin_i(int pin, unsigned char val) {
  if (pin >= 0) {
    bool state = val & 0x01;
    digitalWrite(pin, !state);
  }
}

// Set UART1 to UBX only (disable the NMEA noise)
static const uint8_t setUART1[] = {
  0xb5, 0x62, 0x06, 0x00, 0x14, 0x00,
  0x01, 0x00, 0x00, 0x00, 0xC0, 0x08, 0x00, 0x00, 0x80, 0x25, 0x00, 0x00,
  0x01, 0x00, 0x01, 0x00, 0x00, 0x00, 0x00, 0x00
  };
static const int len_setUART1 = 26;

// Configure Time Pulse - set freqPeriod and freqPeriodLock to 60Hz (0000003C)
static const uint8_t setTimePulse_60Hz[] = {
  0xb5, 0x62, 0x06, 0x31, 0x20, 0x00,
  0x00, 0x01, 0x00, 0x00, 0x32, 0x00, 0x00, 0x00, 0x3C, 0x00, 0x00, 0x00, 0x3C, 0x00, 0x00, 0x00,
  0x00, 0x00, 0x00, 0x80, 0x00, 0x00, 0x00, 0x80, 0x00, 0x00, 0x00, 0x00, 0x29, 0x00, 0x00, 0x00
  };
// Configure Time Pulse - set freqPeriod and freqPeriodLock to 500Hz (000001F4)
static const uint8_t setTimePulse_500Hz[] = {
  0xb5, 0x62, 0x06, 0x31, 0x20, 0x00,
  0x00, 0x01, 0x00, 0x00, 0x32, 0x00, 0x00, 0x00, 0xF4, 0x01, 0x00, 0x00, 0xF4, 0x01, 0x00, 0x00,
  0x00, 0x00, 0x00, 0x80, 0x00, 0x00, 0x00, 0x80, 0x00, 0x00, 0x00, 0x00, 0x29, 0x00, 0x00, 0x00
  };
// Configure Time Pulse - set freqPeriod and freqPeriodLock to 1000Hz (000003E8)
static const uint8_t setTimePulse_1kHz[] = {
  0xb5, 0x62, 0x06, 0x31, 0x20, 0x00,
  0x00, 0x01, 0x00, 0x00, 0x32, 0x00, 0x00, 0x00, 0xE8, 0x03, 0x00, 0x00, 0xE8, 0x03, 0x00, 0x00,
  0x00, 0x00, 0x00, 0x80, 0x00, 0x00, 0x00, 0x80, 0x00, 0x00, 0x00, 0x00, 0x29, 0x00, 0x00, 0x00
  };
// Configure Time Pulse - set freqPeriod and freqPeriodLock to 10000Hz (00002710)
static const uint8_t setTimePulse_10kHz[] = {
  0xb5, 0x62, 0x06, 0x31, 0x20, 0x00,
  0x00, 0x01, 0x00, 0x00, 0x32, 0x00, 0x00, 0x00, 0x10, 0x27, 0x00, 0x00, 0x10, 0x27, 0x00, 0x00,
  0x00, 0x00, 0x00, 0x80, 0x00, 0x00, 0x00, 0x80, 0x00, 0x00, 0x00, 0x00, 0x29, 0x00, 0x00, 0x00
  };
// Configure Time Pulse - set freqPeriod and freqPeriodLock to 100000Hz (000186A0)
static const uint8_t setTimePulse_100kHz[] = {
  0xb5, 0x62, 0x06, 0x31, 0x20, 0x00,
  0x00, 0x01, 0x00, 0x00, 0x32, 0x00, 0x00, 0x00, 0xA0, 0x86, 0x01, 0x00, 0xA0, 0x86, 0x01, 0x00,
  0x00, 0x00, 0x00, 0x80, 0x00, 0x00, 0x00, 0x80, 0x00, 0x00, 0x00, 0x00, 0x29, 0x00, 0x00, 0x00
  };
// Configure Time Pulse - set freqPeriod and freqPeriodLock to 1000000Hz (000F4240)
static const uint8_t setTimePulse_1MHz[] = {
  0xb5, 0x62, 0x06, 0x31, 0x20, 0x00,
  0x00, 0x01, 0x00, 0x00, 0x32, 0x00, 0x00, 0x00, 0x40, 0x42, 0x0F, 0x00, 0x40, 0x42, 0x0F, 0x00,
  0x00, 0x00, 0x00, 0x80, 0x00, 0x00, 0x00, 0x80, 0x00, 0x00, 0x00, 0x00, 0x29, 0x00, 0x00, 0x00
  };
static const int len_setTimePulse = 38;

// Set Nav Mode to Portable
static const uint8_t setNavPortable[] = {
  0xB5, 0x62, 0x06, 0x24, 0x24, 0x00, 0xFF, 0xFF, 0x00, 0x03, 0x00, 0x00, 0x00, 0x00, 0x10, 0x27, 0x00, 0x00, 
  0x05, 0x00, 0xFA, 0x00, 0xFA, 0x00, 0x64, 0x00, 0x2C, 0x01, 0x00, 0x00, 0x00, 0x00, 0x00, 0x00, 0x00, 0x00, 
  0x00, 0x00, 0x00, 0x00, 0x00, 0x00 };

// Set Nav Mode to Pedestrian
static const uint8_t setNavPedestrian[] = {
  0xB5, 0x62, 0x06, 0x24, 0x24, 0x00, 0xFF, 0xFF, 0x03, 0x03, 0x00, 0x00, 0x00, 0x00, 0x10, 0x27, 0x00, 0x00, 
  0x05, 0x00, 0xFA, 0x00, 0xFA, 0x00, 0x64, 0x00, 0x2C, 0x01, 0x00, 0x00, 0x00, 0x00, 0x00, 0x00, 0x00, 0x00, 
  0x00, 0x00, 0x00, 0x00, 0x00, 0x00 };

// Set Nav Mode to Airborne <1G
static const uint8_t setNavAir[] = {
  0xB5, 0x62, 0x06, 0x24, 0x24, 0x00, 0xFF, 0xFF, 0x06, 0x03, 0x00, 0x00, 0x00, 0x00, 0x10, 0x27, 0x00, 0x00, 
  0x05, 0x00, 0xFA, 0x00, 0xFA, 0x00, 0x64, 0x00, 0x2C, 0x01, 0x00, 0x00, 0x00, 0x00, 0x00, 0x00, 0x00, 0x00, 
  0x00, 0x00, 0x00, 0x00, 0x00, 0x00 };
static const int len_setNav = 42;

// Set GNSS Config to GPS + Galileo + GLONASS + SBAS (Causes the M8 to restart!)
static const uint8_t setGNSS[] = {
  0xb5, 0x62, 0x06, 0x3e, 0x3c, 0x00,
  0x00, 0x20, 0x20, 0x07,
  0x00, 0x08, 0x10, 0x00, 0x01, 0x00, 0x01, 0x01,
  0x01, 0x01, 0x03, 0x00, 0x01, 0x00, 0x01, 0x01,
  0x02, 0x04, 0x08, 0x00, 0x01, 0x00, 0x01, 0x01,
  0x03, 0x08, 0x10, 0x00, 0x00, 0x00, 0x01, 0x01,
  0x04, 0x00, 0x08, 0x00, 0x00, 0x00, 0x01, 0x03,
  0x05, 0x00, 0x03, 0x00, 0x00, 0x00, 0x01, 0x05,
  0x06, 0x08, 0x0e, 0x00, 0x01, 0x00, 0x01, 0x01 };
static const int len_setGNSS = 66;

// Send message in u-blox UBX format
// Calculates and appends the two checksum bytes
// Doesn't add the 0xb5 and 0x62 sync chars (these need to be included at the start of the message)
void sendUBX(const uint8_t *message, const int len) {
  int csum1 = 0; // Checksum bytes
  int csum2 = 0;
  for (int i=0; i<len; i++) { // For each byte in the message
    mySerial.write(message[i]); // Write the byte
    if (i >= 2) { // Don't include the sync chars in the checksum
      csum1 = csum1 + message[i]; // Update the checksum bytes
      csum2 = csum2 + csum1;
    }
  }
  csum1 = csum1 & 0xff; // Limit checksums to 8-bits
  csum2 = csum2 & 0xff;
  mySerial.write((uint8_t)csum1); // Send the checksum bytes
  mySerial.write((uint8_t)csum2);
}
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

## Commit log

2020-03-27 Added the BOM
    [BOM.ods, LMG1025_Flasher_Shield.brd, LMG1025_Flasher_Shield.sch]
2020-03-27 Added the LED and SiPM waveforms

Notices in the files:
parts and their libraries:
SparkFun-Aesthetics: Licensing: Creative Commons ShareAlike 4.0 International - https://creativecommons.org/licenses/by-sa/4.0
